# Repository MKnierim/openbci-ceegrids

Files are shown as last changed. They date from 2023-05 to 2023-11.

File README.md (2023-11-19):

# openbci-ceegrids
Collecting brain signals from the ear - affordably and reliably with gelled around-the-ear EEG electrodes (cEEGrids) and the OpenBCI ExG biosignal amplification system.

This repository contains the materials and documentation of this cEEGrid adapter for the use with the OpenBCI Cyton + Daisy boards. 

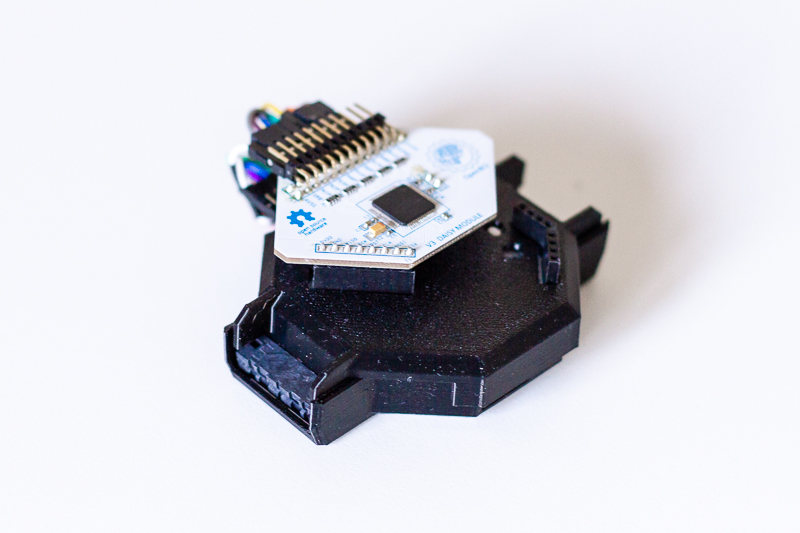
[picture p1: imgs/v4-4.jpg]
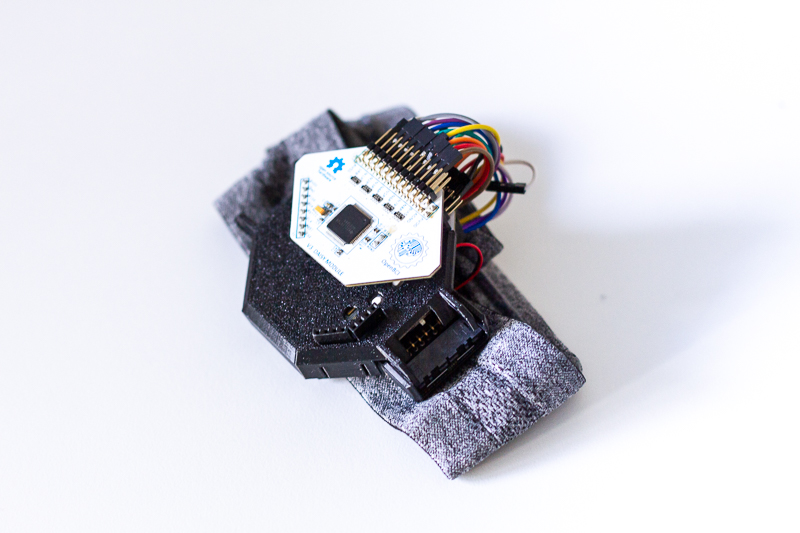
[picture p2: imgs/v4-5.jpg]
  

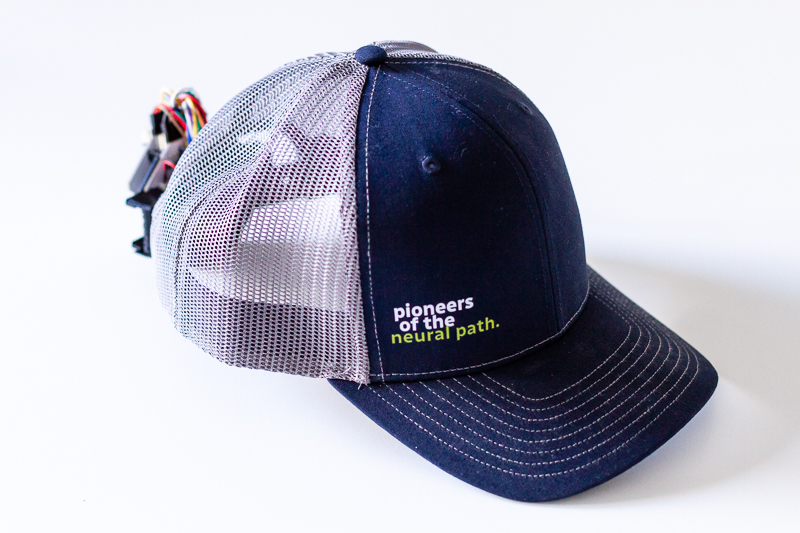
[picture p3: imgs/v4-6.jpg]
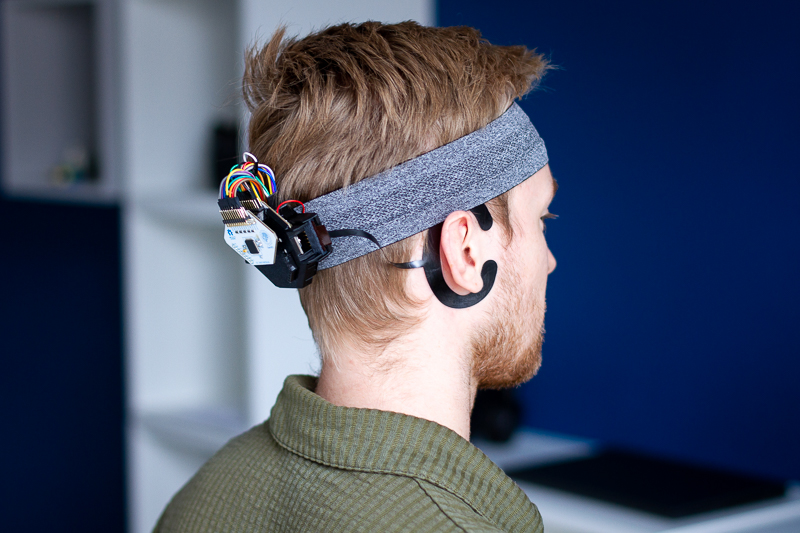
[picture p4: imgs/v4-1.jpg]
 

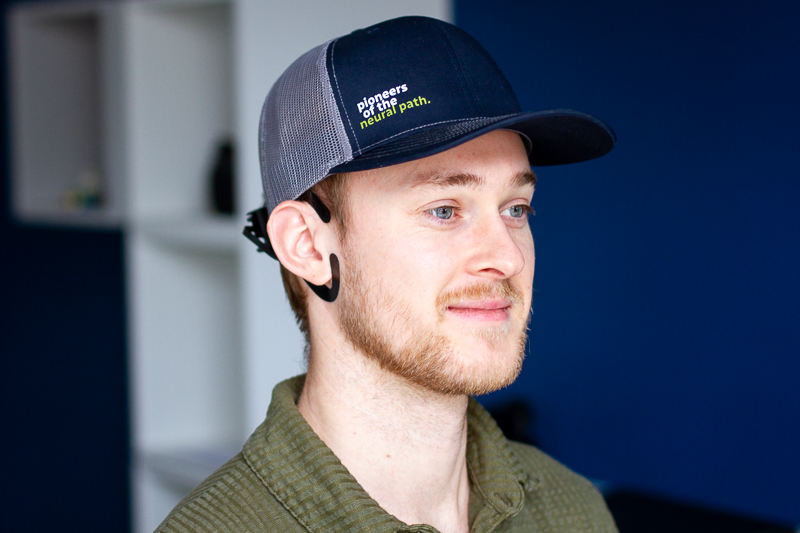
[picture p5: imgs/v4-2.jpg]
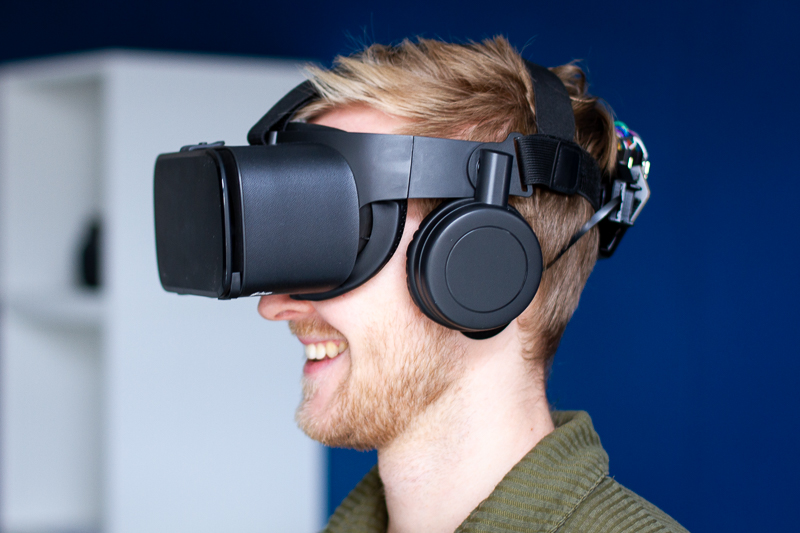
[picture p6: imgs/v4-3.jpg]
 

## Version Updates

This fourth version of the OpenBCI cEEGrid Adapter features:

- **Better Battery Access & Storage:** by taking away the bottom coverage slightly, users can more easily (dis-) connect a battery for charging.
- **Sturdier Body:** By improving tolerances, wall thickness and locking mechanisms, the cover is now much stronger.
- **Better Usability with Baseball Caps:** Through a re-design of the bottom clip, the system can now be used with baseball caps and headbands more easily and reliably.

- The initial technical evaluation of the system has been published in the journal [Brain-Computer Interfaces in 2021](https://doi.org/10.1080/2326263X.2021.1972633)
- For the documentation of the cEEGrid development please refer to the [cEEGrid developers website](https://uol.de/psychologie/abteilungen/ceegrid) or the publication by [Debener et al. 2015](https://www.nature.com/articles/srep16743).
- The project is part of the [KIT Earables Community](https://earables.teco.edu/)
- We will keep making all the materials and documentation available. To make the system more readily available, we also offer to source the materials for you. So if you'd like to save some time, just check out [this website](https://exgtools.expeeeriments.io/).

<a href="https://exgtools.expeeeriments.io/" target="_blank">
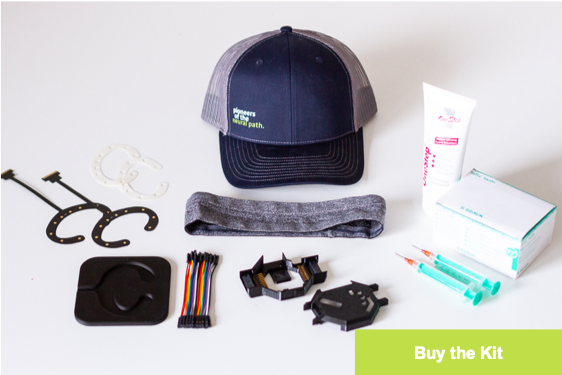
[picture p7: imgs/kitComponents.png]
Components of the OpenBCI-cEEGrid System
	
</a>

<a href="https://exgtools.expeeeriments.io/" target="_blank">
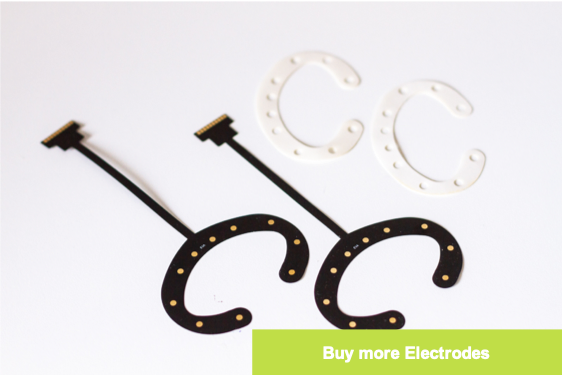
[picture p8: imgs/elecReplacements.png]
Gold-plated cEEGrid Replacement Electrodes
	
</a>

------

## Materials

| Amount | Part   Description                                                  | Instance /   Reference                                                                                               |
|--------|---------------------------------------------------------------------|----------------------------------------------------------------------------------------------------------------------|
| 1      | OpenBCI Cyton Board + Daisy Shield   (Biosignal Acquisition Boards) | Available from <a href="https://shop.openbci.com/collections/frontpage/products/cyton-daisy-biosensing-boards-16-channel?variant=38959256526" target="_blank">OpenBCI</a>              |
| 2      | cEEGrid Electrodes                                                  | Gold-Plated cEEGrids from <a href="https://exgtools.expeeeriments.io/" target="_blank">us</a> or Silver/Silver-Chloride cEEGrids through <a>sales@tmsi.com</a>; Check <a href="https://doi.org/10.1002/nano.202100345" target="_blank">Kurniawan et al. 2022</a> for a material comparison                                          |
| 1      | cEEGrid Sticker Applicator Form                              	   | Custom [3D-Print Files](./stl/) available in this repository                   |
| 2      | Printed   Circuit Boards                                            | Custom [PCB File](./pcb/) available in this repository; Can be manufactured on demand, e.g. at   https://aisler.net/                                                                                                                                                                 |
| 1      | Re-designed Cyton + Daisy Board Mounts                              | Custom [3D-Print Files](./stl/) available in this repository                   |
| 2      | Mini Edge Card Socket                                               | SAMTEC MB1-120-01-L-S-01-SL-N –   configurable at https://www.samtec.com/products/mb1                                |
| 20     | Pin Headers                                                         | Here we used a 10-pin angled SMD header, with 2.54 inch pitch, e.g. available from Harwin Inc. (MPN: M20-8891045) |
| 20     | Jumper Cables                                                       | Here we used short (3 inch) female/female jumper wires, e.g. available at   https://www.adafruit.com/product/1951  |
| 1      | Lithium Ion Polymer Battery - 3.7v 500mAh (JST-PH Connector)        | Available for example at: https://www.adafruit.com/product/1578 |

------

## Assembly & Use Instructions
The kit is comprised of three main components: (1) The OpenBCI Cyton microcontroller with the Daisy 
shield that enables the low-cost mobile biosignal acquisition (e.g. EEG, ECG, or EMG), (2) the cEEGrid electrodes, a set 
of flex-printed electrodes in a c-shaped form that can be placed around a person’s ear using adhesives, and 
(3) the printed circuit board (PCB) that transmits the signal from the applied cEEGrids to an amplifier (the adapter).

### Manufacturing the Components
To produce the plastic components (bottom and top board covers and cEEGrid sticker applicator - [3D-Print Files](./stl/)), FDM 3D-printing can be used 
with a standard 0.4 mm nozzle diameter and 0.2 mm layer height. Rather slow print speeds (e.g. 40 mm/s) should be used as the parts have fine details.

To assemble a cEEGrid adapter PCB, three parts are required, a contact point that connects to the cEEGrid pins (2mm pitch – 
used here is a mini edge card socket by the company SAMTEC), a PCB, and a set of male  or female pin headers with 2.54mm pitch 
(10 pins, single row). The parts can be joined using a soldering iron. To facilitate the soldering of the mini edge card socket 
to the PCB and to lower the risk of bridges it is recommended that every second pin (but starting with the first pin) of the card 
socket is removed before assembling the connector. Extensive instructions for this assembly and for the use of the cEEGrids are 
provided by the cEEGrid developers at: https://uol.de/neuropsychologie/howtoconnect.

### Assembly of the Kit
#### Channel Selection
Before you get started with the assembly, you need to decide which cEEGrid electrodes you want to use in your recording.
Each cEEGrid electrode comes with 10 electrodes (so 20 in total on both ears), but the OpenBCI Cyton+Daisy can only record from
up to 16 channels (+ REF & GND electrodes). Therefore, you need to decide which electrodes to use. For starters, we recommend 
the following default layout that provides fairly even coverage by excluding channel L3 & R3, and using channel L6 as REF and R6 as GND. 
A similar configuration was used in the validation study in [Brain-Computer Interfaces in 2021](https://doi.org/10.1080/2326263X.2021.1972633) for the cEEGrid OpenBCI combination.
If you want to highlight the configuration that you used in a publication, you may use the [PowerPoint](./res/) from this repository for a figure.

#### Connecting the Adapter PCB
The figure below shows how you should route the jumper cables from the adapter PCB to the Cyton+Daisy boards for the configuration mentioned above.

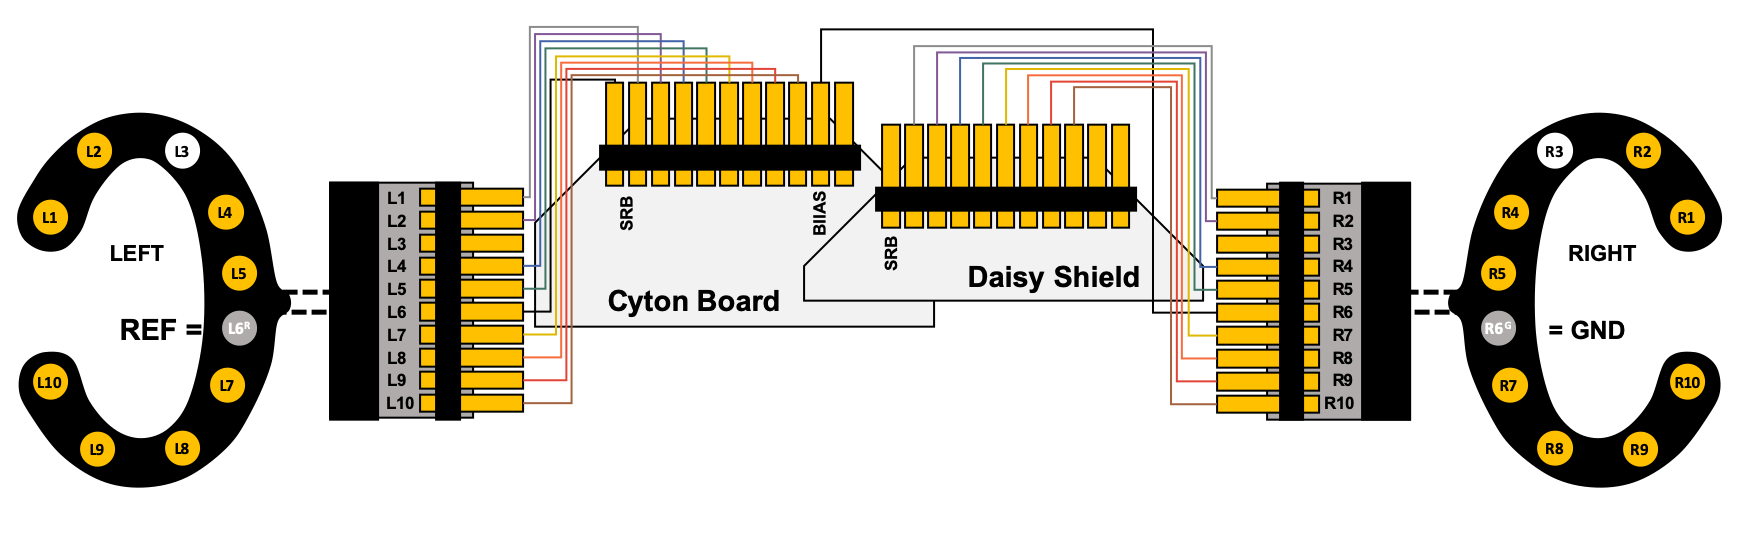
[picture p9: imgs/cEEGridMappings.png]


We recommend connecting the left ear to the Cyton pins (channel 1-8 in the OpenBCI GUI) and the right ear 
to the Daisy pins (channel 9-16 in the OpenBCI GUI). We also recommend maintaining the colour coding to keep 
track of which electrodes are being used and which are left out (see a screenshot of the OpenBCI GUI below.

Start by placing the connector PCBs in their respective slots. Gently pull on the edges of these slots to allow the PCBs to slide in.

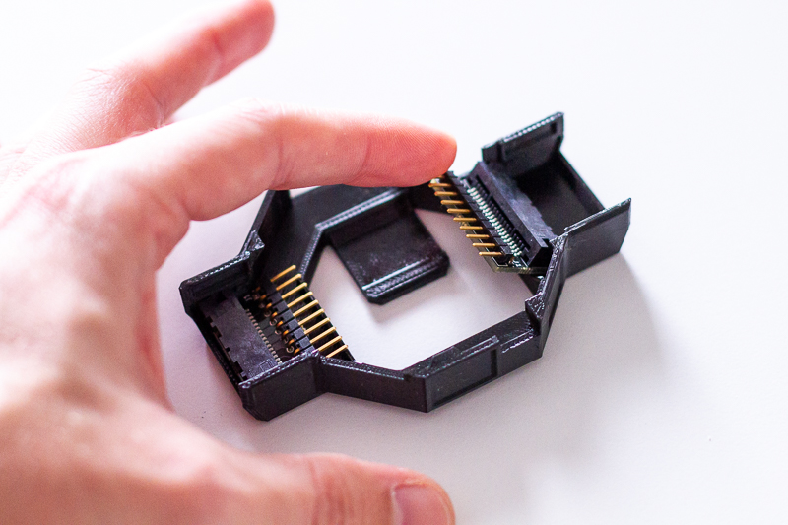
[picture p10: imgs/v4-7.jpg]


Then connect the jumper cables. Make sure to route the jumper wires in a way that the cables will run below the Cyton board (not above it).
To set REF & GND, connect the designated electrodes/pins (here R4a and R4b) to the bottom SRB (for REF) and bottom BIAS (for GND) pins on the Cyton. Beware that the Cyton and Daisy boards need to be connected using a y-splitter cable that comes with the Cyton+Daisy kit (or can be purchased in the OpenBCI shop at: https://shop.openbci.com/products/y-splitter-cable).
This is the default setup for the Cyton+Daisy to collect EEG data (see also: https://docs.openbci.com/GettingStarted/Biosensing-Setups/EEGSetup/)

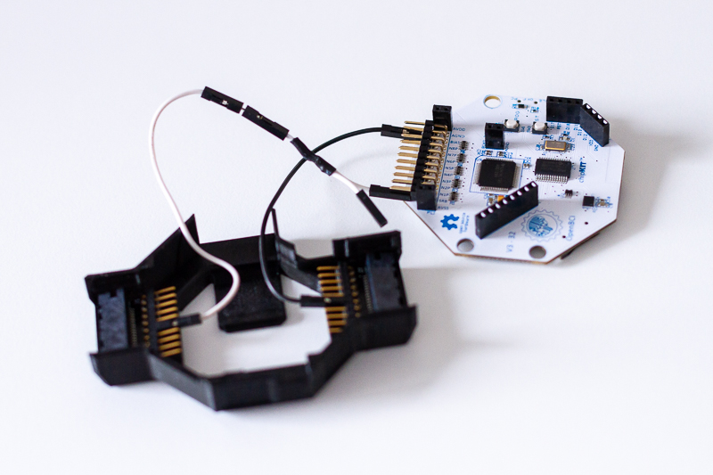
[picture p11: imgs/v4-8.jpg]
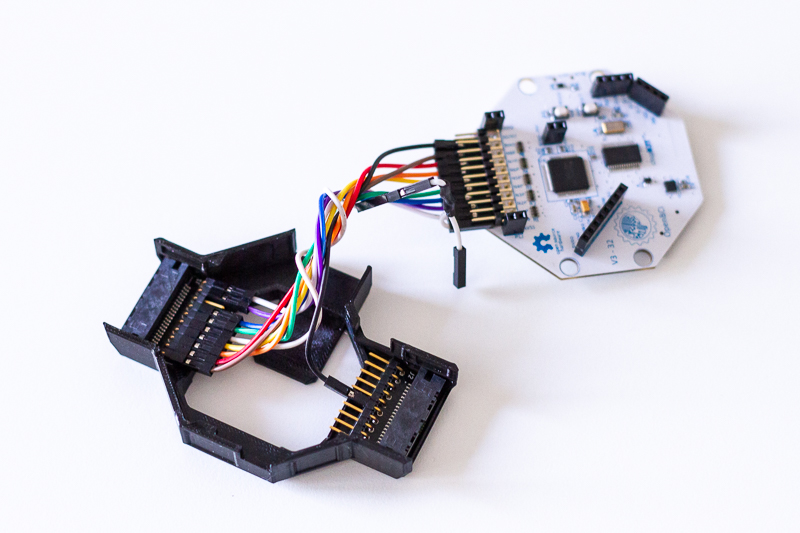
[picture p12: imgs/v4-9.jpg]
 

Next, put the top enclosure on and stack the Daisy on top of the Cyton board. 
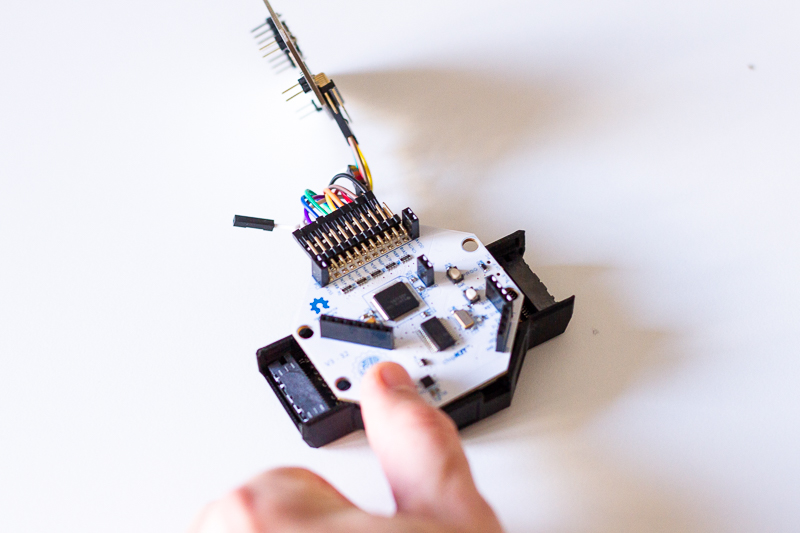
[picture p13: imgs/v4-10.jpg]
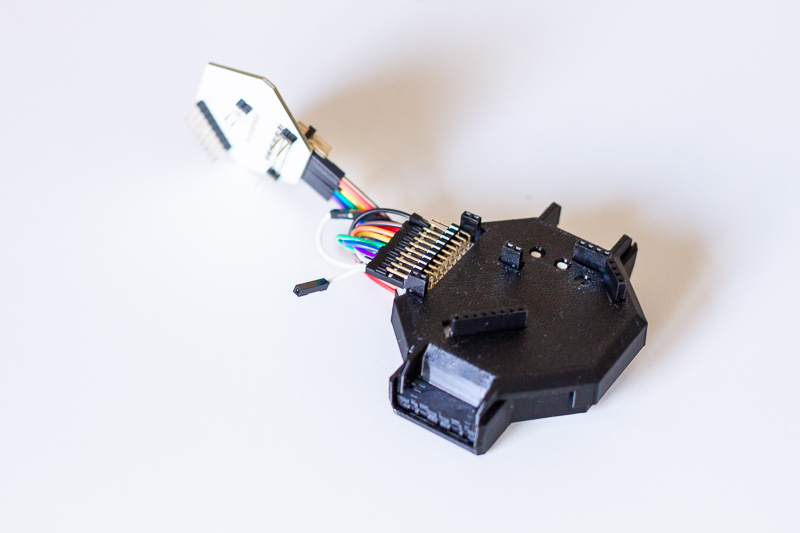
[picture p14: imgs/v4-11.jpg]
 

Almost there now, you just need to add a battery.

#### Connecting the Battery
As a power supply, use a 400 or 500mAh lithium-ion rechargeable battery pack. Simply plug the battery into the JST-PH connector that is accesible from the bottom of the case. Then, stow away the battery in the case by sliding it in through the large opening on the bottom cover. 

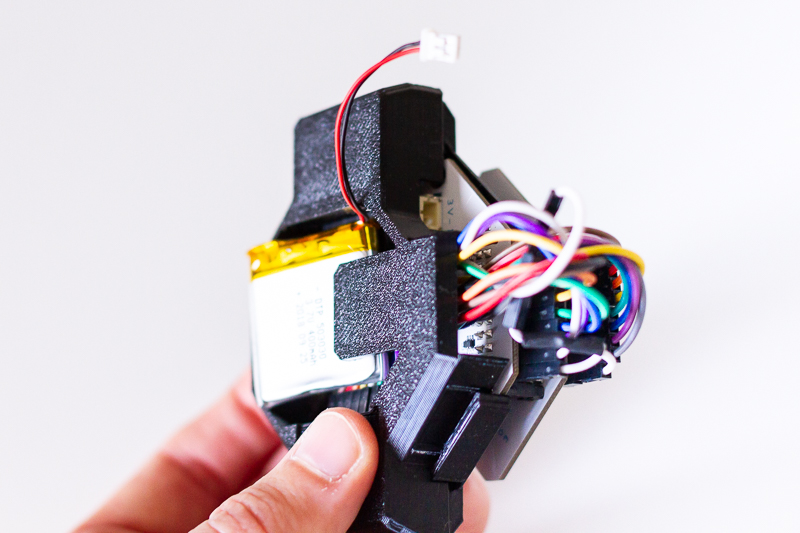
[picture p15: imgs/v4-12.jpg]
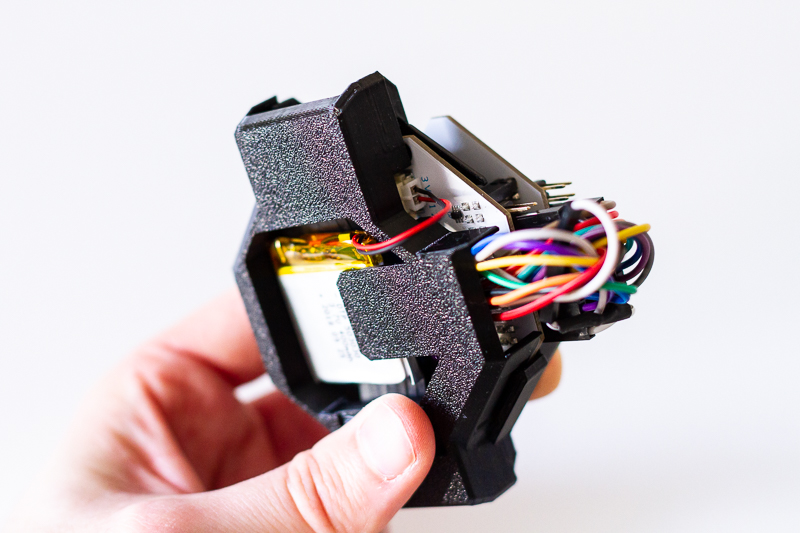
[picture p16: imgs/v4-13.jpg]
 

Voilà, you are set up, attach to your hat and get recording!

#### Wearing Solution
Attach the system to your preferred mounting solution (a headband, cap, hat, VR lenses, or similar) and start your recording. For laboratory recordings we recommend using a simple headband. Here, especially a thin one works perfectly and does not produce a warming sensation. For field settings, we recommend using a baseball cap to blend more naturally in everyday situations.

 

### Setting up a Recording
Haven't used cEEGrids before? No problem, we got you covered with the use instructions below. 

Important note: We are using gold-plated cEEGrids whereas the original cEEGrids used an Ag/AgCl plating that is commonly used in EEG systems. The use and design is otherwise exactly the same, so you can also decide which ones to use.

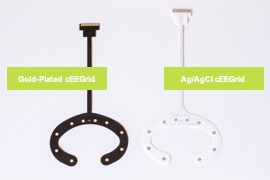
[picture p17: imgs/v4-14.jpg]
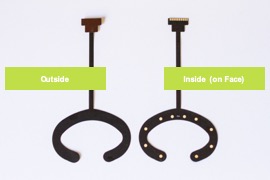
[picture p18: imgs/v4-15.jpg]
 

Worried about the recording suitability? Recent research (https://doi.org/10.1002/nano.202100345) highlights lower impedance of gold (Au) electrodes in the 1-1000Hz region than Ag/AgCl (but higher impedances <1Hz). So, for most EEG and EMG recordings, these gold-plated electrodes are a fantastic alternative!

#### Attaching cEEGrids
Ok, so now that you have your kit set up and are ready to conduct a recording, you need to prepare and apply the cEEGrid electrodes. Here, we are following the instructions by the cEEGrid developers (see: https://uol.de/neuropsychologie/howtouse). They have also produced a set of video instructions: https://uol.de/en/psychology/neurophysiology/resources/ceegrid-video-tutorial. For completeness, we detail the cEEGrid application steps here as well. 

In a first step, make sure you have two cEEGrids ready. That means, you should attach a new set of stickers with the help of the sticker applicator. Make sure, to attach the sticker on the correct side (the side where the gold pads are exposed). Place the cEEGrid in the applicator form, remove the liner on one side of the sticker and attach it from the outside inwards. Make sure that the holes are leaving the electrode pads uncovered.

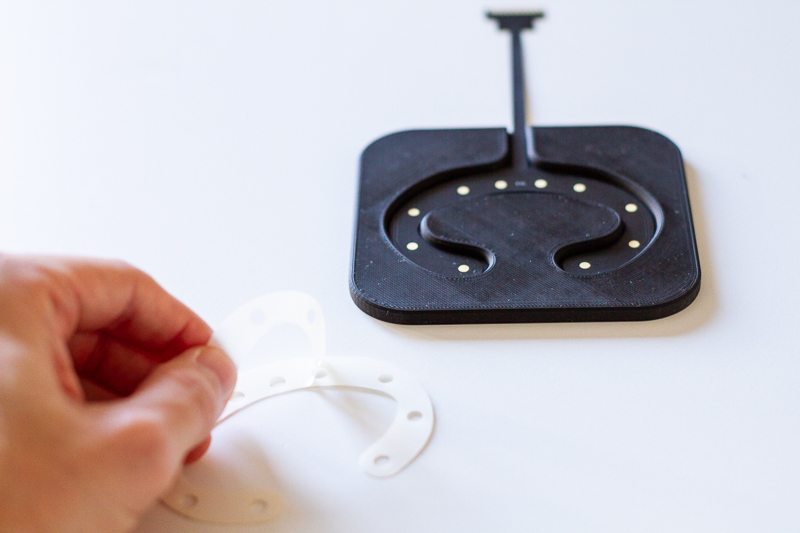
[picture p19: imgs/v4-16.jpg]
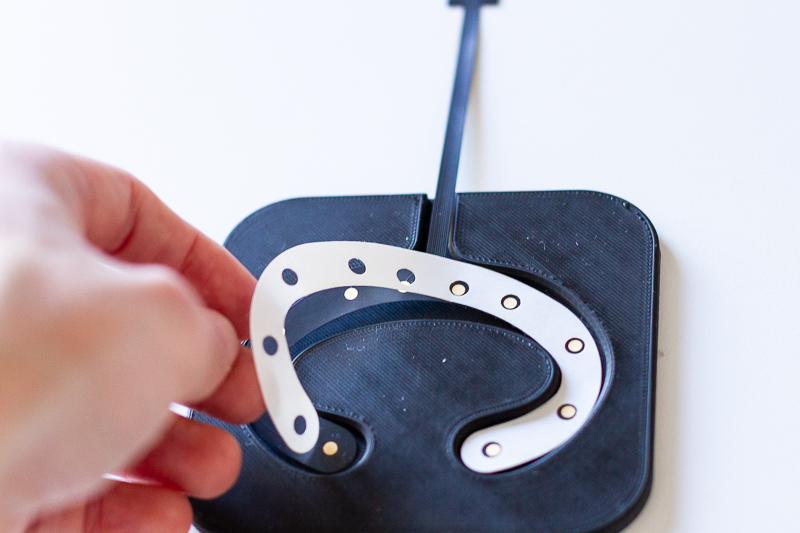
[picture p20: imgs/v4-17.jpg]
 

Next, take off the other side of the sticker and leave the electrode lying on a table with the adhesive exposed. We prefer adding the gel after this step to not accidentally remove it when taking off the sticker liner afterwards. Add a lentil-sized amount of electrolyte to each individual electrode pad using the syringe. We use Abrasiv Plus from OneStep, but other electrolytes should work as well.

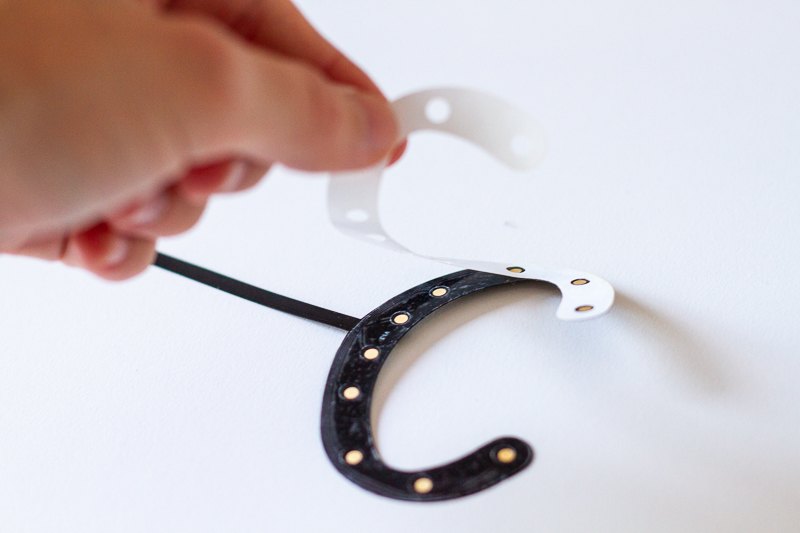
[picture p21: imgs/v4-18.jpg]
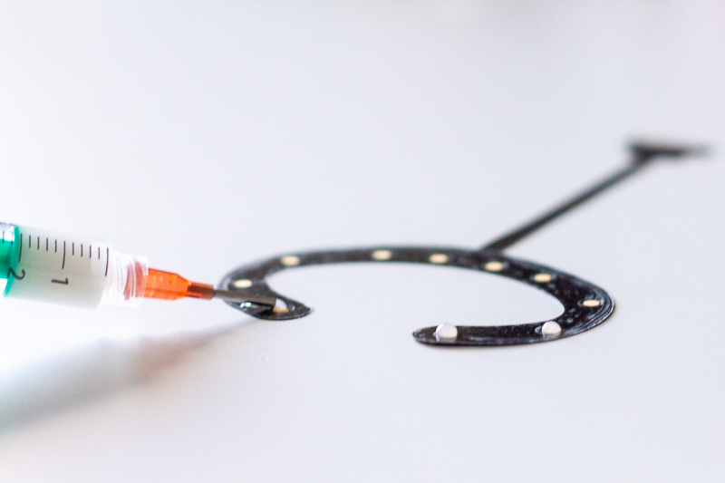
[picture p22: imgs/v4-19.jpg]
 

Now, get the participant's skin ready and apply the electrode. It is recommended to clean the skin around the ear with an alcohol pad to remove oily residues that can lower the signal-to-noise ratio (SNR) of your recordings due to higher impedances at the electrode-skin interface. Ask the participant to keep hair away from the ear and gently apply the cEEGrid. The grid is perfectly positioned when it is not touching the pinna (outer-ear).

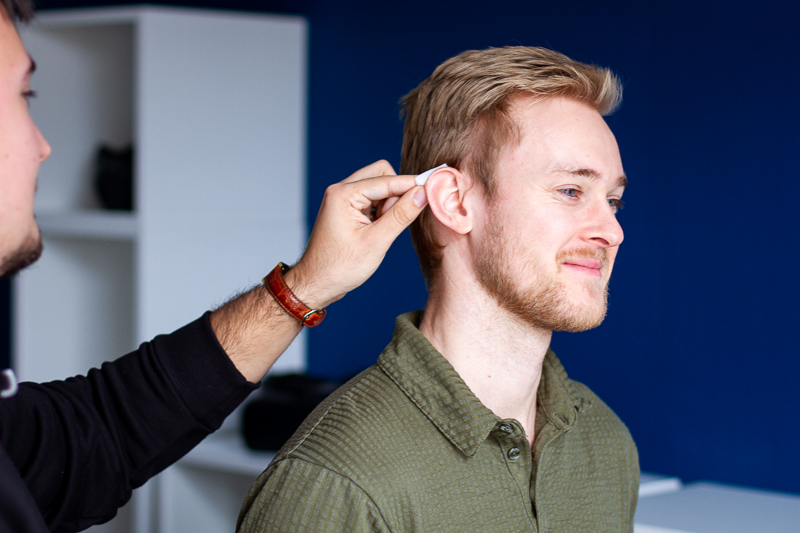
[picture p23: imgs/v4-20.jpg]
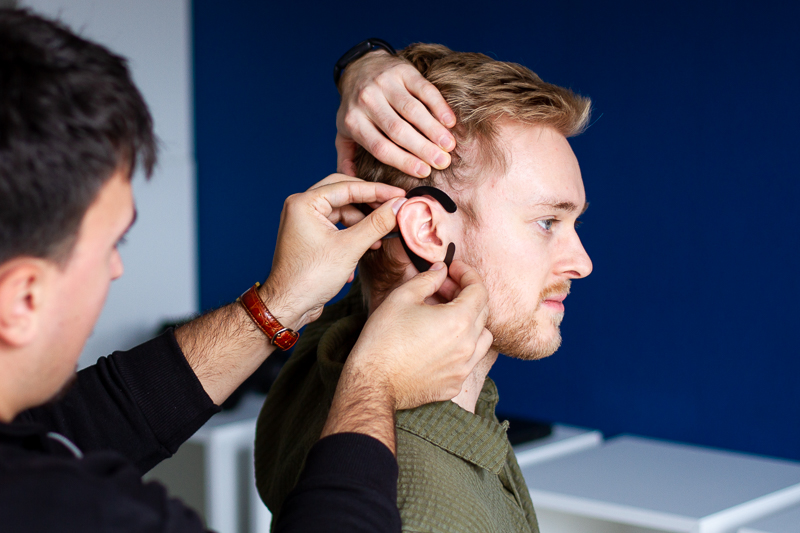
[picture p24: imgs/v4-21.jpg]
 

Plug in the cEEGrids (gold plates facing towards the head) into the edge card sockets and you are ready to start recording! 

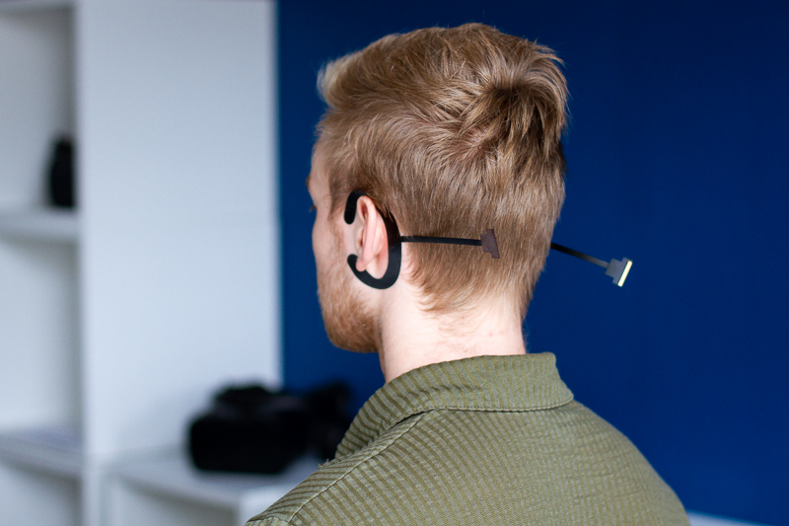
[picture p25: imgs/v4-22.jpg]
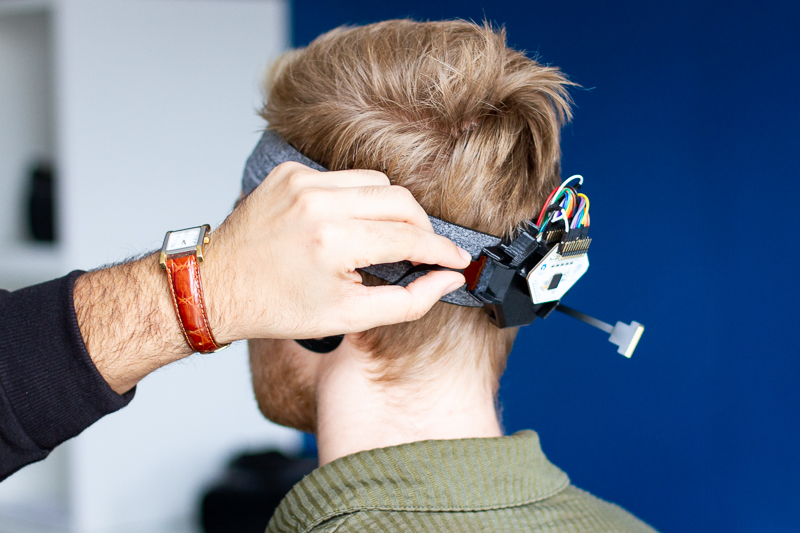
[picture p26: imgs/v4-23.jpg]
 

#### Starting a Recording
To start a recording, open OpenBCI GUI with the 16 channel configuration and connect the Cyton+Daisy boards. You can click "Start Data Stream" to see the signals coming in. Before you record the data, you should conduct some initial signal quality checks. 

As a first indicator, you will see, if all channels are showing similar signals and amplitudes. As the cEEGrid electrodes are close to each other, the signals will be similar (but not exactly the same!). If you see individual flat or heavily fluctuating channels in isolation, these electrode pads might need a bit more gel. If two or more channels next to each other are flat, you probably have accidentally created a gel bridge, shortening the two channels. In that case, you unfortunately have to detach the cEEGrid, clean off the gel, and then re-apply it.

As another signal quality check, you should inspect the channel impedances to get a more accurate SNR metric. Switch to the "Cyton Signal" widget and click the "Check all Channels" button. This checks the impedance on each channel iteratively (see also: https://docs.openbci.com/Software/OpenBCISoftware/GUIDocs/#impedance-testing). Beware that the impedances may take a little while to settle, similarly to cap-based EEG. With good skin cleaning and adequate amount of gel you should be getting impedances between 10 and 50 kOhm.

Ok, and that is it! When you are satisfied with your impedances and signal qualities, click the "Start Data Stream" button again and enjoy collecting cEEGrid data! If you are looking for inspiration, check out some of the documented cases below!

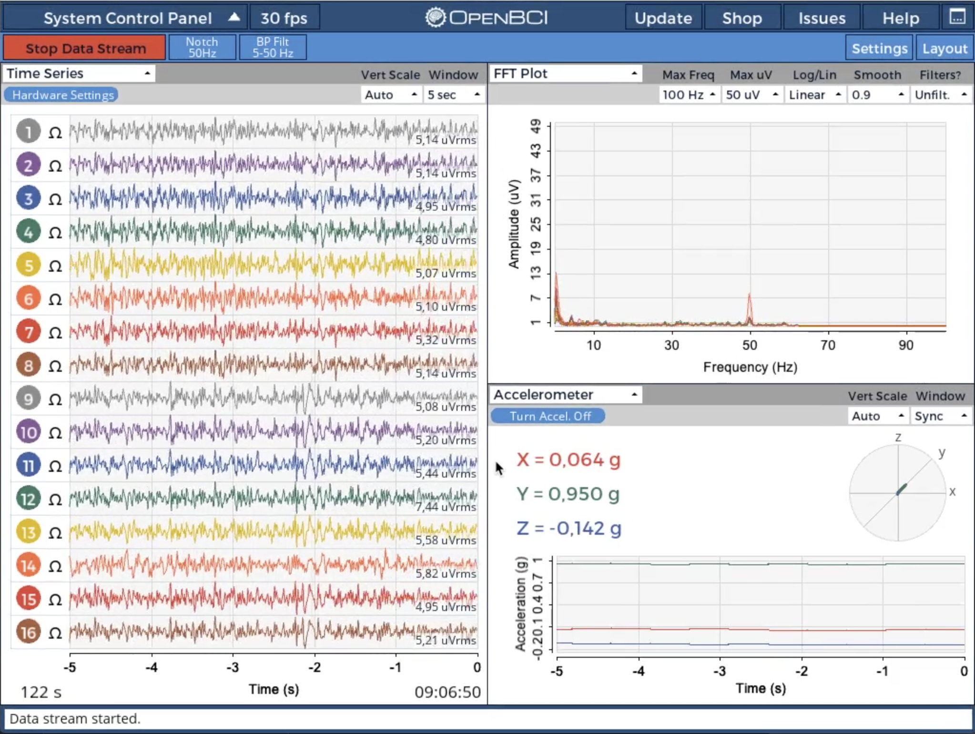
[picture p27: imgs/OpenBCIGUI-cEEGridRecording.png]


#### Cleaning / Re-using the cEEGrids
If handled properly a cEEGrid can be re-used a few times. After removal from the partcipant, carefully remove the used adhesive sticker. Try to not scratch the electrode pads during removal. Then, clean the grid very gently under running water. Make sure to rinse off all the gel. Do not rub the electrode pads and do not use any chemicals for cleaning. Dry the cleaned cEEGrid gently with a tissue and store it in a dark place, protected from light.

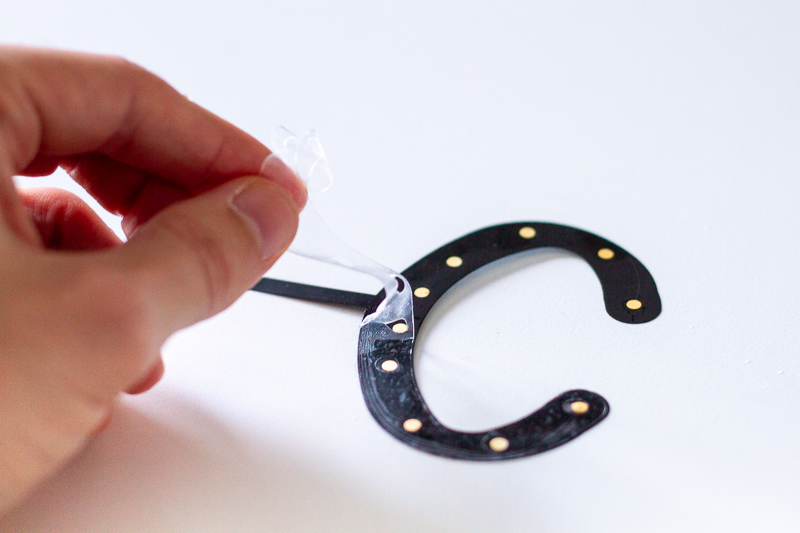
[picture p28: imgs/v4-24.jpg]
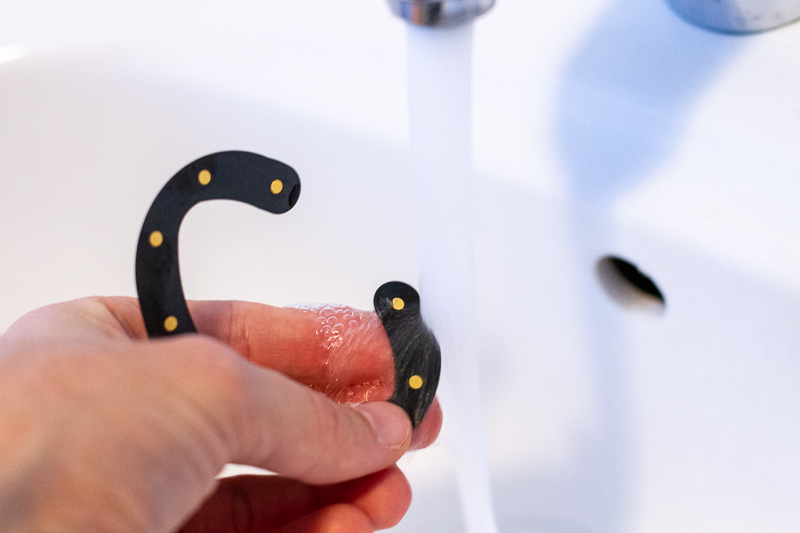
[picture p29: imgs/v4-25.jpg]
 

------

## Application Examples
### Documented Capabilities
This recording system has been demonstrated to replicate well-known and previously documented neural activity findings (Knierim et al. 2021a). 
Specifically, the former authors documented the blocking of visual input from closing the eyes in occipital brain regions 
(the so-called Berger effect), and the modulation of higher frequency ranges from changes in mental workload. 
These observations have previously been established for the cEEGrid electrodes with other amplifiers (e.g., the MBT Smarting Mobi) (Bleichner & Debener 2017, Debener et al. 2015, Wascher et al 2019). 
In addition, other relatively large amplitude phenomena have been observed with the OpenBCI-cEEGrid system. 
Thereby, the distinctive patterns of various facial muscle activities have been found to be captured and differentiated well (Knierim et al. 2021b, 2021c).

### Use Case: Daytime Bruxism detection
Here, we want to highlight a promising and relevant use case for this system, which is detecting bruxism events. 
Bruxism is the repetitive clenching or grinding of the teeth, a condition associated with multiple physiological and 
psychological health issues, including fractures, erosion of the teeth, headaches, stress, and anxiety. 
Bruxism occurs during the day and the night (sleep bruxism). Even though prevalence for awake bruxism (AB) is relatively 
high among adults (22-30% - compared to sleep bruxism - SB: 1-15%), its detection and intervention have been researched sparsely. 
AB detection challenges are that bruxing events need to be differentiated from a variety of other facial activities and 
that daily recordings need to occur inconspicuously and ergonomically. For this reason, previous work (Knierim et al. 2021c) explored whether 
the cEEGrids can be used with the OpenBCI amplifier as an effective approach to detect bruxing events using machine learning. 
While this previous work reported promising classification performances (F1-Scores of 0.73 to 0.90 for identifying 
posed bruxing events vs. 13 other posed facial activities), it relied on single-session within-subject classification, 
which imposes a central limitation towards generalizability and applicability of the detection approach for real-life 
AB detection. 

Thus, to further explore the utility of the herein reported sensing system, we extended this previous work by a more 
complex, multi-session data collection. One participant completed an experiment three times on three separate days in 
which 28 facial activities were posed (two of which are jaw clenching activities - see the following figure). 
The experimental protocol was highly similar to that reported in (Knierim et al. 2021c).

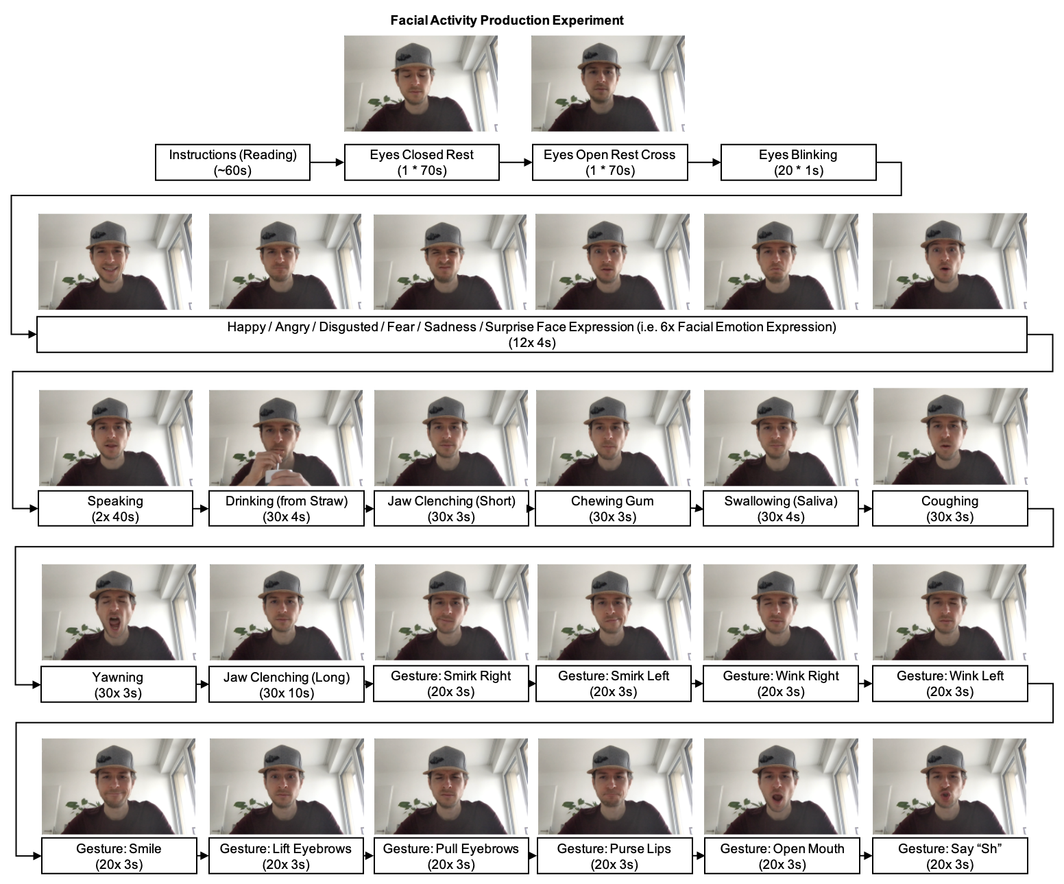
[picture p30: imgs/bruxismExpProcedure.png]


The recorded signals were labeled according to the corresponding experiment phase and trial (with a shift of 350ms for 
onset/offset of the facial activity per trial). Afterwards, to mimic the process of a live (online) classification system, 
the data were epoched as non-overlapping 1-second windows. An epoch was considered to contain a bruxism event if ≥50% 
of the epoch samples were previously labeled as containing a bruxism episode. Each epoch was then pre-processed using: 
(1) mean-centering of the channel, (2) band-pass filtering (5-62 Hz IIR), and (3) notch filtering (50 Hz IIR). 
Next, a range of features was extracted for each channel and epoch: (1) Hjorth Activity, (2) Hjorth Complexity, 
(3) Hjorth Mobility, (4) Absolute Amplitude Maximum, (5) Absolute Amplitude Sum, (6) Higuchi Fractal Dimension, 
(7) Petrosian Fractal Dimension. Overall, that lead to a dataset of 9944 epochs (first recording = 3350, 
second recording = 3315, third recording = 3279) and 16 (channels) * 7 features = 112 features. Two of the recordings 
were first combined to create a diversified training data set. The third recording was held out as a test data set. 
To optimize the classifier, five-fold stratified cross-validation was performed using the training data. 
SMOTE oversampling was used to deal with the imbalanced distribution of classes. All the features were z-standardized 
and classified with an AdaBoost model. Finally, the model was assessed by predicting the unseen test data from the 
third recording session. This resulted in an F1-Score of 0.73 (Recall: 0.74, Precision: 0.72) for the prediction of 
bruxing events vs all other 26 classes.

These results indicate that, while further improvements can be made, the OpenBCI-cEEGrid recording system appears as a 
viable solution to observe the occurrence of bruxing events. In the spirit of sharing the content of our research, 
the [recorded data and the Python code](./code/) for a simple live bruxism detection system are provided with the article. 

Take a look at this video to see the live biofeedback system in action:

<a href="./video/bruxismDemo.mp4">
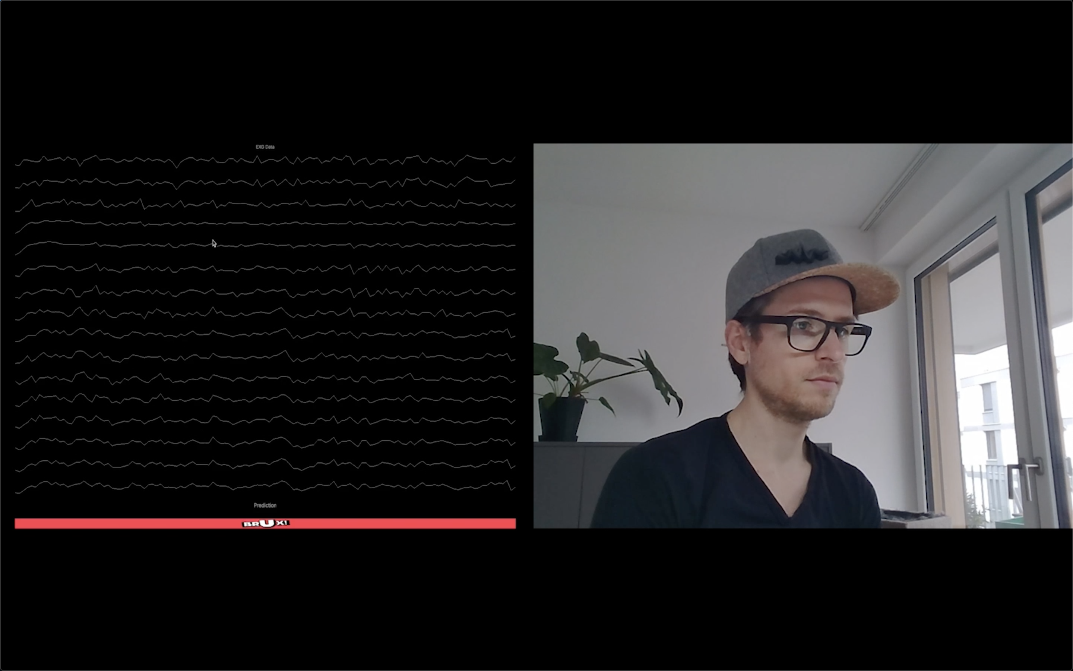
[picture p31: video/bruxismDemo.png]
	
</a>

------

## Publications
### With this System
- Knierim, M. T., Bleichner, M. G., & Reali, P. (2023). A Systematic Comparison of High-End and Low-Cost EEG Amplifiers for Concealed, Around-the-Ear EEG Recordings. Sensors, 23(9), 4559. https://doi.org/10.3390/s23094559
- Knierim, M.T., Schemmer, M., Bauer, N. (2022)a. A Simplified Design of a cEEGrid Ear-Electrode Adapter for the OpenBCI Biosensing Platform. HardwareX. [e00357] DOI: <a href="https://doi.org/10.1016/j.ohx.2022.e00357" target="_blank">https://doi.org/10.1016/j.ohx.2022.e00357</a>
- Knierim, M. T., Bartholomeyczik, K., Nieken, P., & Weinhardt, C. (2022)b. Could we Predict Flow from Ear-EEG?. In 2022 10th International Conference on Affective Computing and Intelligent Interaction Workshops and Demos (ACIIW) 2022, 1-6. DOI: <a href="https://doi.org/10.1109/ACIIW57231.2022.10086037" target="_blank">https://doi.org/10.1109/ACIIW57231.2022.10086037</a>
- Bartholomeyczik, K., Knierim, M. T., Nieken, P., Seitz, J., Stano, F., & Weinhardt, C. (2022) Flow in Knowledge Work: An Initial Evaluation of Flow Psychophysiology Across Three Cognitive Tasks. Proceedings of the NeuroIS Retreat 2022, 30-41. DOI: <a href="https://doi.org/10.1007/978-3-031-13064-9_3" target="_blank">https://doi.org/10.1007/978-3-031-13064-9_3</a>
- Knierim, M. T., Berger, C., & Reali, P. (2021)a. Open-source concealed EEG data collection for Brain-computer-interfaces - neural observation through OpenBCI amplifiers with around-the-ear cEEGrid electrodes. Brain-Computer Interfaces, 8(4), 161-179. DOI: <a href="https://doi.org/10.1080/2326263X.2021.1972633" target="_blank">https://doi.org/10.1080/2326263X.2021.1972633</a>
- Knierim, M. T., Schemmer, M., & Perusquía-Hernández, M. (2021)b. Exploring the recognition of facial activities through around-the-ear electrode arrays (cEEGrids). Proceedings of the NeuroIS Retreat 2021, 47-55. DOI: <a href="https://doi.org/10.1007/978-3-030-88900-5_6" target="_blank">https://doi.org/10.1007/978-3-030-88900-5_6</a>
- Knierim, M. T., Schemmer, M., & Woehler, D. (2021)c. Detecting Daytime Bruxism Through Convenient and Wearable Around-the-Ear Electrodes. Proceedings of the International Conference on Applied Human Factors and Ergonomics 2021, 26-33. DOI: <a href="https://doi.org/10.1007/978-3-030-80091-8_4" target="_blank">https://doi.org/10.1007/978-3-030-80091-8_4</a>

### With other Amplifiers
- Debener, S., Emkes, R., De Vos, M., and Bleichner, M. (2015). Unobtrusive ambulatory EEG using a smartphone and flexible printed electrodes around the ear. Sci. Rep. 5, 1–11. DOI: <a href="https://doi.org/10.1038/srep16743" target="_blank">https://doi.org/10.1038/srep16743</a>
- Bleichner, M. G., and Debener, S. (2017). Concealed, unobtrusive ear-centered EEG acquisition: Ceegrids for transparent EEG. Front. Hum. Neurosci. 11, 1–14. DOI: <a href="https://doi.org/10.3389/fnhum.2017.00163" target="_blank">https://doi.org/10.3389/fnhum.2017.00163</a>
- Mikkelsen, K. B., Ebajemito, J. K., Bonmati-Carrion, M. A., Santhi, N., Revell, V. L., Atzori, G., della Monica, C., Debener, S. Dijk, D. J., Sterr, A., and de Vos, M. (2019). Machine-learning-derived sleep–wake staging from around-the-ear electroencephalogram outperforms manual scoring and actigraphy. J. Sleep Res. 28, 2. DOI: <a href="https://doi.org/10.1111/jsr.12786" target="_blank">https://doi.org/10.1111/jsr.12786</a>
- Sterr A., Ebajemito, J. K., Mikkelsen, K. B., Bonmati-Carrion, M. A., Santhi, N., della Monica, C., Grainger, L., Atzori, G., Revell, V., Debener, S., Dijk, D. J., De Vos, M. (2018). Sleep EEG derived from behind- the-ear electrodes (cEEGrid) compared to standard polysomnography: A proof of concept study. Front. Hum. Neurosci. 12, 1–9. DOI: <a href="https://doi.org/10.3389/fnhum.2018.00452" target="_blank">https://doi.org/10.3389/fnhum.2018.00452</a>
- Wascher, E., Arnau, S., Reiser, J. E., Rudinger, G., Karthaus, M., Rinkenauer, G., Dreger, F., and Getzmann, S. (2019). Evaluating Mental Load During Realistic Driving Simulations by Means of Round the Ear Electrodes. Front. Neurosci. 13, 1–11. DOI: <a href="https://doi.org/10.3389/fnins.2019.00940" target="_blank">https://doi.org/10.3389/fnins.2019.00940</a>
- Getzmann, S., Reiser, J. E., Karthaus, M., Rudinger, G., & Wascher, E. (2021). Measuring correlates of mental workload during simulated driving using ceegrid electrodes: a test–retest reliability analysis. Frontiers in neuroergonomics, 2, 729197. <a href="https://doi.org/10.3389/fnrgo.2021.729197" target="_blank">https://doi.org/10.3389/fnrgo.2021.729197</a>
- Garrett, M., Debener, S., & Verhulst, S. (2019). Acquisition of subcortical auditory potentials with around-the-ear cEEGrid technology in normal and hearing impaired listeners. Frontiers in neuroscience, 13, 730. DOI: <a href="https://doi.org/10.3389/fnins.2019.00730" target="_blank">https://doi.org/10.3389/fnins.2019.00730</a>
- Jaeger, M., Mirkovic, B., Bleichner, M. G., & Debener, S. (2020). Decoding the attended speaker from EEG using adaptive evaluation intervals captures fluctuations in attentional listening. Frontiers in Neuroscience, 14, 603. DOI: <a href="https://doi.org/10.3389/fnins.2020.00603" target="_blank">https://doi.org/10.3389/fnins.2020.00603</a>
- Mirkovic, B., Bleichner, M. G., De Vos, M., & Debener, S. (2016). Target speaker detection with concealed EEG around the ear. Frontiers in neuroscience, 10, 349. DOI: <a href="https://doi.org/10.3389/fnins.2016.00349" target="_blank">https://doi.org/10.3389/fnins.2016.00349</a>
- Nogueira, W., Dolhopiatenko, H., Schierholz, I., Büchner, A., Mirkovic, B., Bleichner, M. G., & Debener, S. (2019). Decoding selective attention in normal hearing listeners and bilateral cochlear implant users with concealed ear EEG. Frontiers in neuroscience, 13, 720. DOI: <a href="https://doi.org/10.3389/fnins.2019.00720" target="_blank">https://doi.org/10.3389/fnins.2019.00720</a>

### Citation
```bib
@article{10.1080/2326263X.2021.1972633,
  title={Open-source concealed EEG data collection for Brain-computer-interfaces-neural observation through OpenBCI amplifiers with around-the-ear cEEGrid electrodes},
  author={Knierim, Michael Thomas and Berger, Christoph and Reali, Pierluigi},
  journal={Brain-Computer Interfaces},
  volume={8},
  number={4},
  pages={161--179},
  year={2021},
  publisher={Taylor \& Francis}
}
```

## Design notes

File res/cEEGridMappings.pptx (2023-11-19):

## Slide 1

L2

L3

Cyton Board

Daisy Shield

SRB

R3

R2

L1

LEFT

REF =

L4

L5

L1

L2

L3

L4

SRB

BIIAS

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
RIGHT

= GND

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
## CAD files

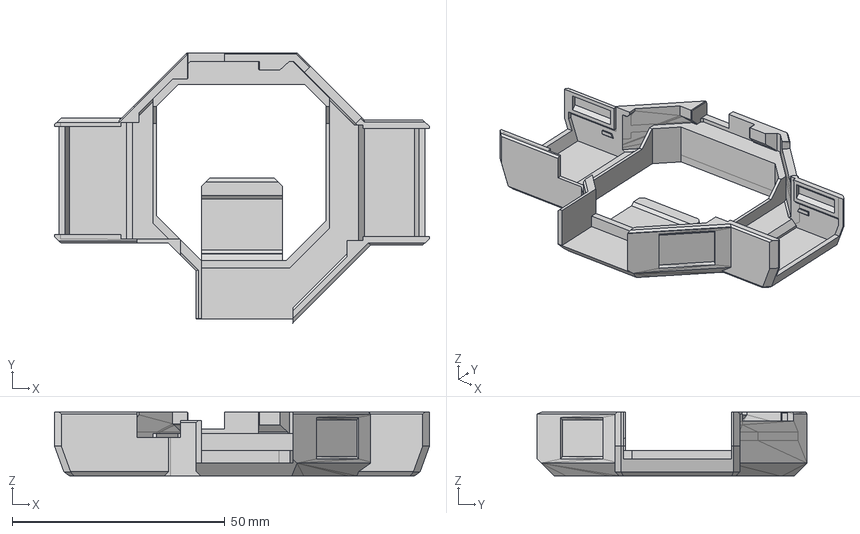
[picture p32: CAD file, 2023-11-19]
stl/Casing_Bottom.step
88.1 x 63.4 x 15.0 mm

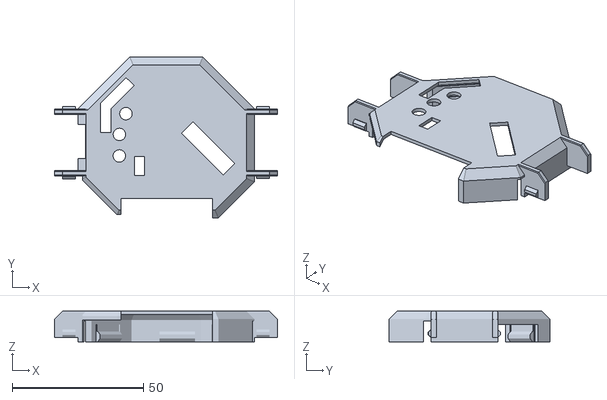
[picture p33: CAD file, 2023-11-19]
stl/Casing_Top.stl
85.1 x 61.4 x 11.7

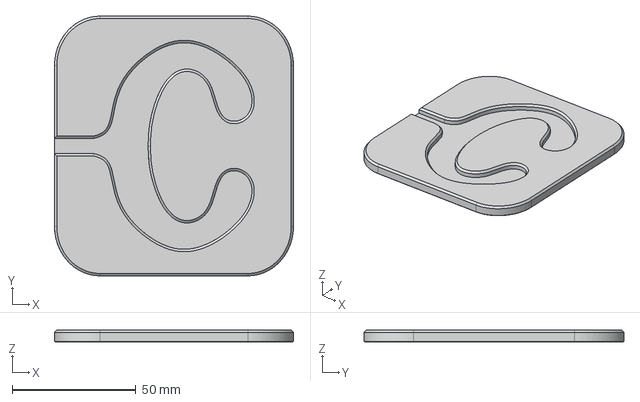
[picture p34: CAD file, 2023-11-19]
stl/cEEGridApplicator.step
96.6 x 105.0 x 5.00 mm

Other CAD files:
stl/Casing_Bottom.stl
stl/cEEGridApplicator.stl

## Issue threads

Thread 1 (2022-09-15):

### ISSUE TITLE
Costs of the materials

### ISSUE THREAD

**Issue by farfalk** [MKnierim/openbci-ceegrids#1]
First things first: thank you so much for sharing your approach!

I'm planning to reproduce your approach in the near future, but I'd like to know the costs (estimated is good enough) of the components and the materials to plan accordingly. Is it possible, and would it be meaningful to you, to list them in the materials section of the readme (https://github.com/MKnierim/openbci-ceegrids#materials)?

**Comment by MKnierim** [comment]
Sure, that seems like a good idea to me too! I have added material cost estimates to the section. Please be advised that these costs might still vary slightly, depending on whether you use manufacturing services or not (incl. material, labor, and postage costs). Also, if you'd prefer to get the materials sent to you altogether in a package, please take a look at this offer: https://exgtools.expeeeriments.io/

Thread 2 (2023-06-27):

### ISSUE TITLE
I can't make contact with the website administrator listed in the readme documents (expeeeriment.io）

### ISSUE THREAD

**Issue by SeanZhang99** [MKnierim/openbci-ceegrids#2]
I want to buy a kit and some more electrodes. But if I directly purchase them, I have to pay double package fees. Besides, I want to know more detail from the developer. I've tried to send emails according to their description in the website, but no response was given for few weeks. So if anyone knows how contact them please tell me. Thankyou!

**Comment by MKnierim** [comment]
Dear SeanZhang99, oh that is unfortunate. Upon checking with my mail provider, it appears that your message was not correctly delivered. However, I have received it and will reply to you by the end of the day!

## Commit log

2022-09-15 Added Material Cost Estimates to README
2022-09-15 Fix error in Materials Table
2023-05-01 Release of V2
    Major changes are:
    - New, single row connector PCB (facilitates mapping of channels)
    - Re-designed the adapter holder to be usable with Ultracortex headset and more flexible with different headsizes
    [ConnectorHolder.stl, ConnectorHousing.stl, CytonCaseClip.stl, M4_Hardware_insert_105dot5_percent.stl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]
2023-05-02 Release V3
    - Better Connector Placement: reducing the distance to the ears and thereby reducing tension on the electrode cables for some participants with larger head sizes.
    - Better Cable Storage: By routing the connector cables inside of the enclosure, artefacts from cable contacts are eliminated, and the overall footprint of the system is reduced.
    - Fewer Components: Through a re-design of the 3D printed components, only two parts need to be printed now (the Cyton+Daisy board cover).
    - Added an exemplary biofeedback application for bruxism detection (from Knierim et al. 2022 - HardwareX).
    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
    [Casing_Bottom.step, Casing_Bottom.stl, Casing_Top.stl, ConnectorHolder.stl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]
2023-11-19 Release of V4
    This fourth version of the OpenBCI cEEGrid Adapter features:
    - Better Battery Access & Storage: by taking away the bottom coverage slightly, users can more easily (dis-) connect a battery for charging.
    - Sturdier Body: By improving tolerances, wall thickness and locking mechanisms, the cover is now much stronger.
    - Better Usability with Baseball Caps: Through a re-design of the bottom clip, the system can now be used with baseball caps and headbands more easily and reliably.
    [Casing_Bottom.step, Casing_Bottom.stl, Casing_Top.stl, cEEGridApplicator.step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]
